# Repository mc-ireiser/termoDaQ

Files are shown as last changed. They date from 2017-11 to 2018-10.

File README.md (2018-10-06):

# termoDaQ

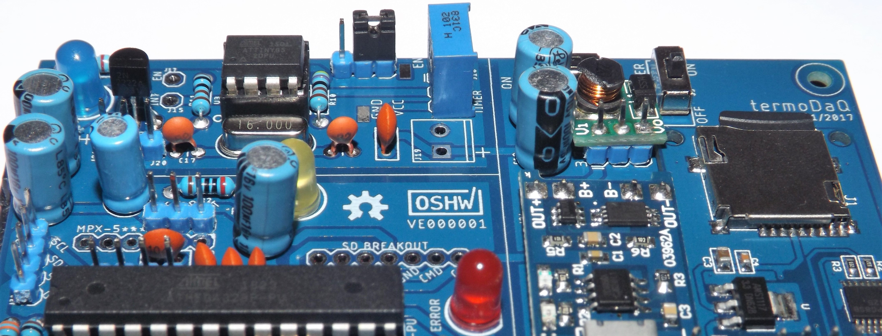
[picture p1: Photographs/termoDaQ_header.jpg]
Header


termoDaQ is a development board based on the [Arduino](https://www.arduino.cc/) architecture, uses an [ATmega328-P](http://ww1.microchip.com/downloads/en/DeviceDoc/Atmel-42735-8-bit-AVR-Microcontroller-ATmega328-328P_Summary.pdf) and an [ATtiny85](http://ww1.microchip.com/downloads/en/DeviceDoc/Atmel-2586-AVR-8-bit-Microcontroller-ATtiny25-ATtiny45-ATtiny85_Datasheet-Summary.pdf) for its operation.

This board was originally designed to help the work of oceanography students, serving as an instrument for the acquisition of physical variables (temperature, pressure) at surface level in bodies of fresh water, in order to detect changes that may affect the flora or fauna of ecosystems, automating the work of making measurements over time.

But it can serve many purposes since it has a connection for GPS receivers, pressure sensor, multiple temperature sensors (internal and external), two additional inputs for any analog sensor (such as rain, flow or UV) and SD card.

The function of the [ATtiny85](http://ww1.microchip.com/downloads/en/DeviceDoc/Atmel-2586-AVR-8-bit-Microcontroller-ATtiny25-ATtiny45-ATtiny85_Datasheet-Summary.pdf) is work as a timer to program the operation cycles of the equipment, reducing the energy consumption, which allows incrementing the operation time when the battery is used. To achieve this, activate and deactivate the sensors area.

The function of the [ATmega328-P](http://ww1.microchip.com/downloads/en/DeviceDoc/Atmel-42735-8-bit-AVR-Microcontroller-ATmega328-328P_Summary.pdf) is to control the sensors area, managing each of them to perform the measurement and data storage processes.

## Operation

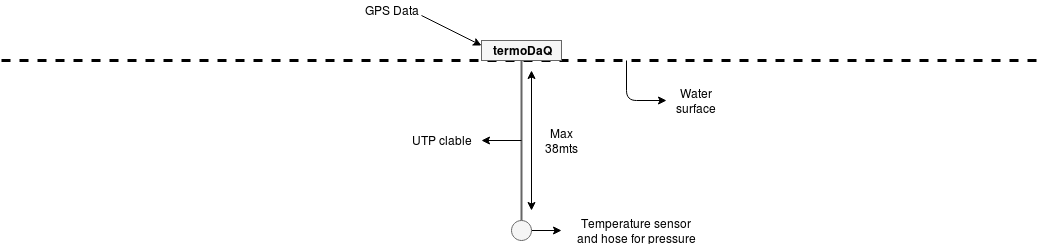
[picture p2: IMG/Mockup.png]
Operation


The board is divided into three parts

1) Power supply.
2) Energy management.
3) Sensors area.

In particular, I'm responsible for developing the energy management and the sensors area.

For the energy management, is used the [ATtiny85](http://ww1.microchip.com/downloads/en/DeviceDoc/Atmel-2586-AVR-8-bit-Microcontroller-ATtiny25-ATtiny45-ATtiny85_Datasheet-Summary.pdf) microcontroller to carry out cycles that enable or disable the sensors, cutting off the power in periods where no measurements are needed.

As for the sensors area, its function is to perform the measurements and store the data. Only one cycle at a time, at the end one signal is sent to the energy management area to cut the power.

## Pinout

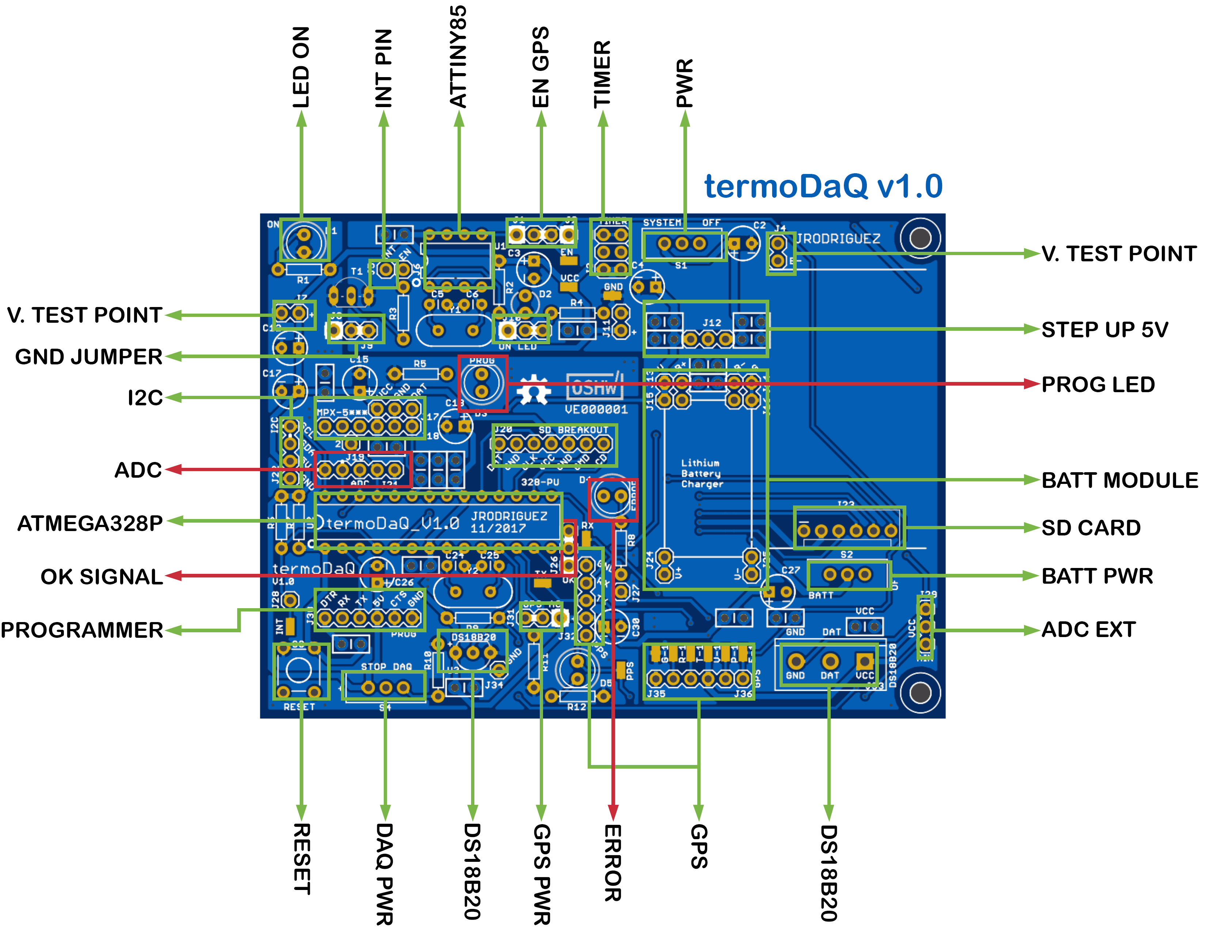
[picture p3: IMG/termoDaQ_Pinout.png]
Pinout


## Board specifications

All the source files are in this repository

- Board Size: 99.82 mm X 73.41 mm (X = 99.82, Y = 73.41)
- Number of layers: 2
- Number of drills: 311
- Number of vias: 47
- Number of signals: 146
- Minimum copper trace width: 0.41 mm
- Consumption: ~ 80mAh (currently under test)

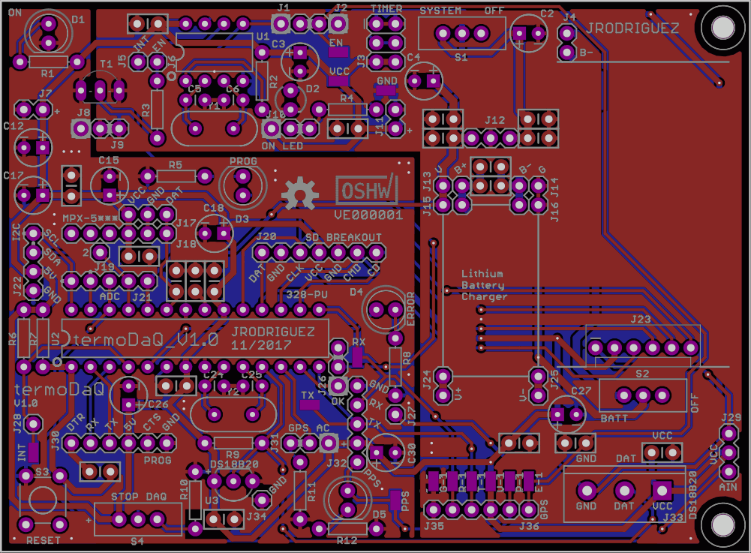
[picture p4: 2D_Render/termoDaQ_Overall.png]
Overall


### ATtiny85

|Name | Value |
| ---------- | ---------- |
|Operating Voltage Range (V) | 1.8 to 5.5 |
|Temperature Range (C) | -40 to 85 |
|CPU Speed (MIPS/DMIPS) | 20 |
|Pin Count | 8 |
|Program Memory Type | Flash |
|Program Memory Size (KB) | 8 |
|SRAM Bytes | 512 |
|Data EEPROM/HEF (bytes) | 512 |
|Digital Communication Peripherals | 1-SPI, 1-I2C |
|Capture/Compare/PWM Peripherals | 5PWM |
|Timers | 2 x 8-bit |
|Number of Comparators | 1 |

### ATmega328P

| Name | Value |
| ---------- | ---------- |
|Operating Supply Voltage | 1.8 V to 5.5 V |
|Temperature Range (C) | - 40 to 85 |
|Maximum Clock Frequency | 20 MHz |
|Pin count | 28 |
|Number of I/Os | 23 I/O |
|Program Memory Type | Flash |
|Program Memory Size | 32 kB |
|Data Bus Width | 8 bit |
|Data RAM Type | SRAM |
|Data RAM Size | 2 kB |
|Data ROM Type | EEPROM |
|Data ROM Size | 1 kB |
|Number of ADC Channels | 6 |
|ADC Resolution | 10 bit |
|Interface Type | I2C, SPI, USART |
|Number of Timers/Counters | 3 Timer |

## Translation

English translation using google translator.

If you wish, you can help me translate the readme file correctly.

## License

Creative Commons Attribution-ShareAlike 4.0 International Public License

Please go to the License section for more information. [Link](https://github.com/mc-ireiser/termoDaQ/tree/master/License)



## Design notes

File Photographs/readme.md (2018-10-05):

# Assembly and operation test

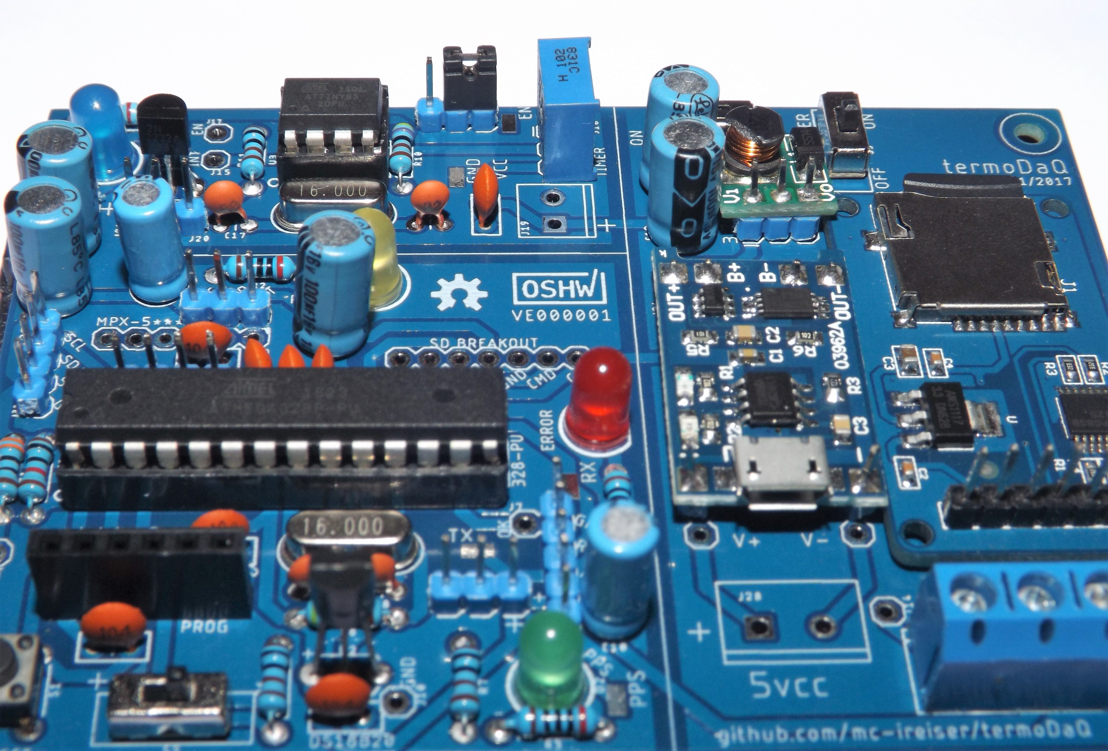
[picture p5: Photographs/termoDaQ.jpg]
Board Assembly


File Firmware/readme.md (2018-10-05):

# Attention

The firmware is under development.

All sensors were tested and work properly. [Picture](https://github.com/mc-ireiser/termoDaQ/blob/master/Photographs/termoDaQ.jpg).

Meanwhile you can perform tests or create your own code based on the [**arduino**](https://www.arduino.cc/reference/en/) architecture.

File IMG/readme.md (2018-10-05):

# Images

## Pinout

Pinout

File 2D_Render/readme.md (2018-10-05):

# 2D Render

2D rendering from source files.

## Top

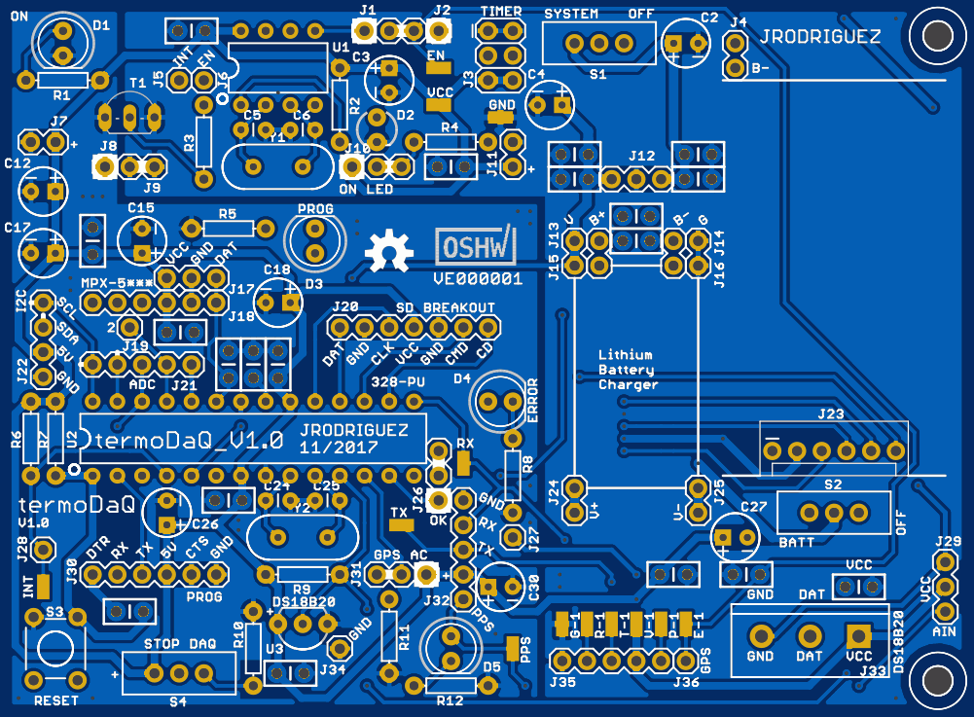
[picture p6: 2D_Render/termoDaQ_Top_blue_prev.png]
Top 2D Render


## Bottom

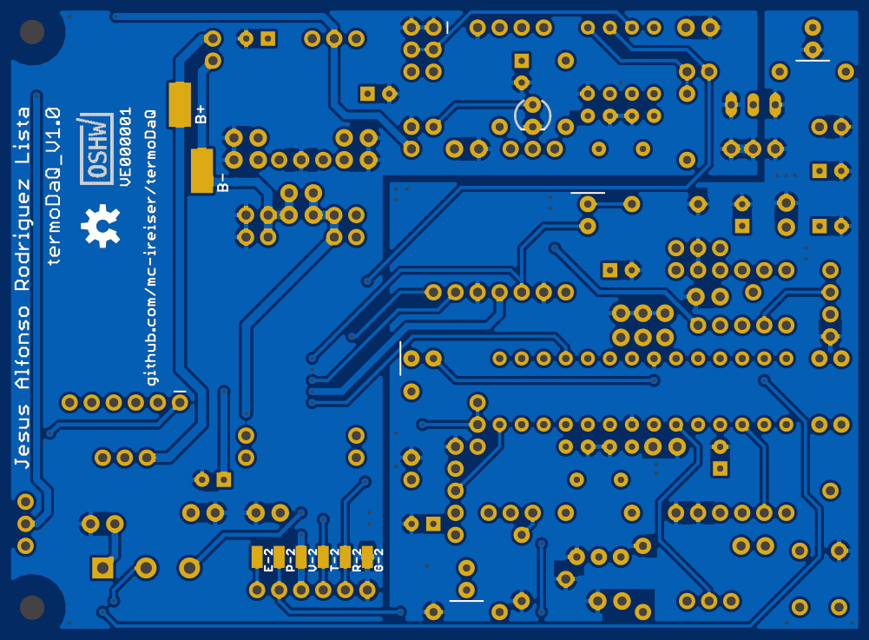
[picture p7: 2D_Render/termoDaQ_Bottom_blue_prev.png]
Bottom 2D Render


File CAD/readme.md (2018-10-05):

# Description of files

- .brd source file with the design of the PCB
- .sch source file with the schematics of the board

These files are licensed under: Creative Commons Attribution-ShareAlike 4.0 International Public License

## Schematics

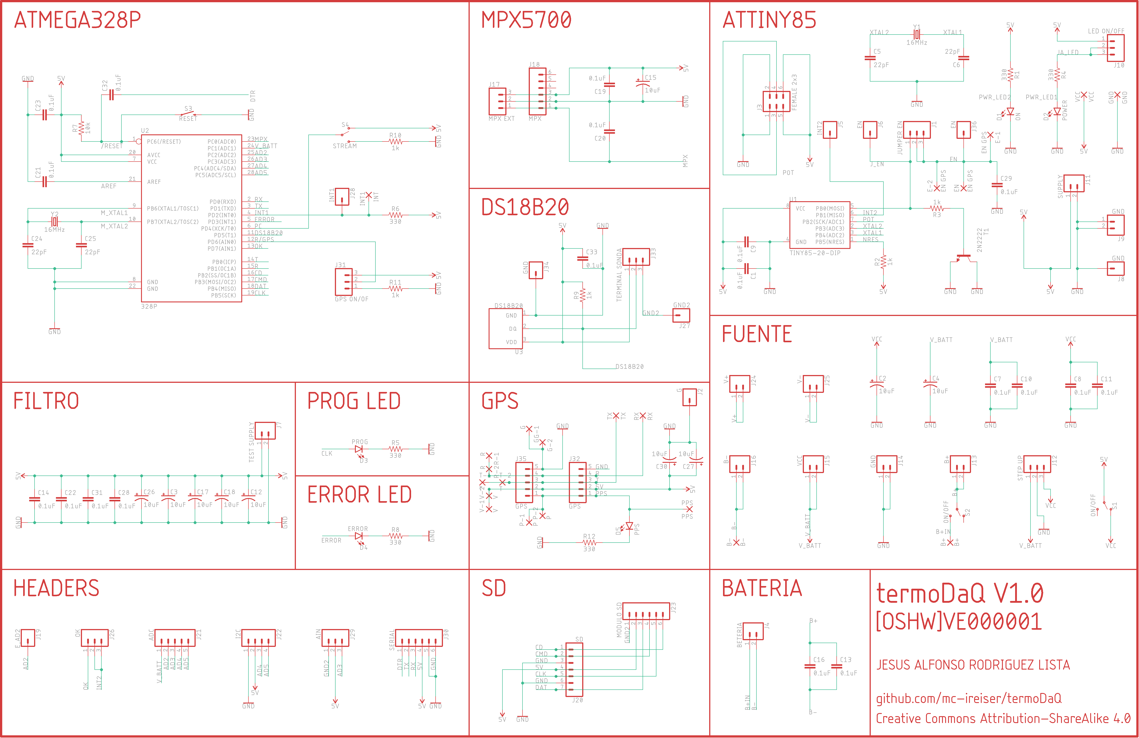
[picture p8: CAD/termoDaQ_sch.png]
Schematics


## Disclaimer

Last updated: October 05, 2018

(the "Service", files contained on this page)

Jesus Rodriguez assumes no responsibility for errors or omissions in the contents on the Service.

In no event shall Jesus Rodriguez be liable for any special, direct, indirect, consequential, or incidental damages or any damages whatsoever, whether in an action of contract, negligence or other tort, arising out of or in connection with the use of the Service or the contents of the Service. Jesus Rodriguez reserves the right to make additions, deletions, or modification to the contents on the Service at any time without prior notice.

This Disclaimer for Jesus Rodriguez is managed by TermsFeed Disclaimer Generator

Jesus Rodriguez does not warrant that the website is free of viruses or other harmful components.

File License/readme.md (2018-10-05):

# License

**termoDaQ** [OSHW] VE000001 by **Jesus Alfonso Rodriguez Lista**, is licensed under:

## Creative Commons Attribution-ShareAlike 4.0 International Public License

- File: `~/Licence/CC BY-SA 4.0.txt` - [read](https://github.com/mc-ireiser/termoDaQ/blob/master/License/CC%20BY-SA%204.0.txt)

- Source: https://creativecommons.org/licenses/by-sa/4.0



## Certified open source hardware

Link: https://certification.oshwa.org/ve000001.html

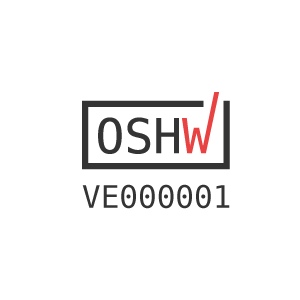
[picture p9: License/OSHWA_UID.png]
OSHWA UID VE000001


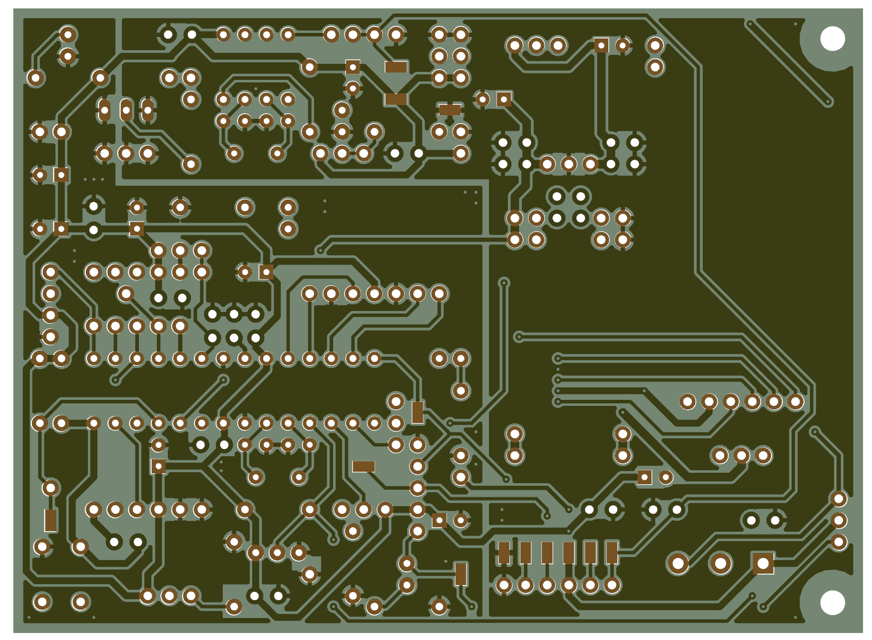
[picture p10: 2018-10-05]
2D_Render/termoDaQ_fr4_no-silk.png

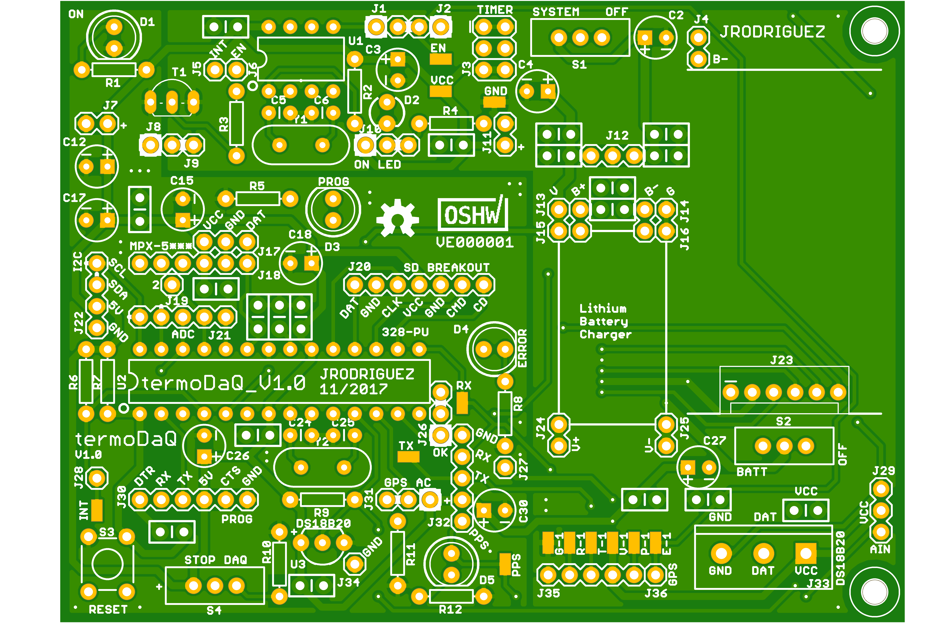
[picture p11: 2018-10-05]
2D_Render/termoDaQ_Top_green_prev.png

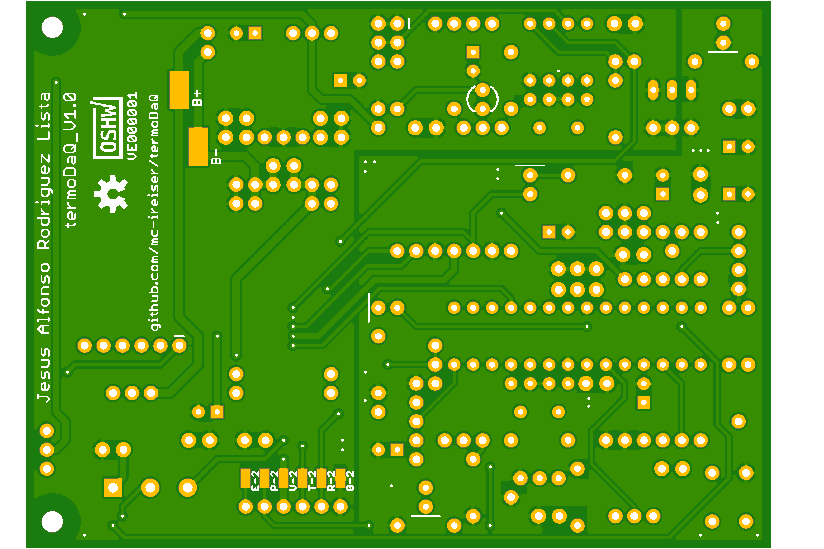
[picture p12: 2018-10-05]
2D_Render/termoDaQ_Bottom_green_prev.png

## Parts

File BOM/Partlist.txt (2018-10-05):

Partlist

Exported from termoDaQ.brd

EAGLE Version 9.1.3 Copyright (c) 1988-2018 Autodesk, Inc.

Assembly variant: 

Part     Value          Package                    Library                     Position (inch)       Orientation

C1       0.1uF          CAP-PTH-SMALL-KIT          SparkFun-Capacitors         (0.8 2.8)             R0
C2       10uF           CPOL-RADIAL-2.5MM-5MM      SparkFun-Capacitors         (2.8 2.75)            R180
C3       10uF           CPOL-RADIAL-2.5MM-5MM      SparkFun-Capacitors         (1.6 2.6)             R90
C4       10uF           CPOL-RADIAL-2.5MM-5MM      SparkFun-Capacitors         (2.25 2.5)            R0
C5       22pF           CAP-PTH-2.54               SparkFun-Capacitors         (1.05 2.4)            R0
C6       22pF           CAP-PTH-2.54               SparkFun-Capacitors         (1.25 2.4)            R0
C7       0.1uF          CAP-PTH-SMALL-KIT          SparkFun-Capacitors         (2.35 2.3)            R180
C8       0.1uF          CAP-PTH-SMALL-KIT          SparkFun-Capacitors         (2.85 2.3)            R0
C9       0.1uF          CAP-PTH-SMALL-KIT          SparkFun-Capacitors         (1.85 2.25)           R0
C10      0.1uF          CAP-PTH-SMALL-KIT          SparkFun-Capacitors         (2.35 2.2)            R180
C11      0.1uF          CAP-PTH-SMALL-KIT          SparkFun-Capacitors         (2.85 2.2)            R0
C12      10uF           CPOL-RADIAL-2.5MM-5MM      SparkFun-Capacitors         (0.2 2.15)            R0
C13      0.1uF          CAP-PTH-SMALL-KIT          SparkFun-Capacitors         (2.6 2.05)            R0
C14      0.1uF          CAP-PTH-SMALL-KIT          SparkFun-Capacitors         (0.4 1.95)            R90
C15      10uF           CPOL-RADIAL-2.5MM-5MM      SparkFun-Capacitors         (0.6 1.95)            R270
C16      0.1uF          CAP-PTH-SMALL-KIT          SparkFun-Capacitors         (2.6 1.95)            R0
C17      10uF           CPOL-RADIAL-2.5MM-5MM      SparkFun-Capacitors         (0.2 1.9)             R0
C18      10uF           CPOL-RADIAL-2.5MM-5MM      SparkFun-Capacitors         (1.15 1.7)            R0
C19      0.1uF          CAP-PTH-SMALL-KIT          SparkFun-Capacitors         (0.755 1.58)          R180
C20      0.1uF          CAP-PTH-SMALL-KIT          SparkFun-Capacitors         (0.95 1.45)           R90
C21      0.1uF          CAP-PTH-SMALL-KIT          SparkFun-Capacitors         (1.05 1.45)           R270
C22      0.1uF          CAP-PTH-SMALL-KIT          SparkFun-Capacitors         (1.15 1.45)           R90
C23      0.1uF          CAP-PTH-SMALL-KIT          SparkFun-Capacitors         (0.95 0.9)            R0
C24      22pF           CAP-PTH-2.54               SparkFun-Capacitors         (1.15 0.9)            R0
C25      22pF           CAP-PTH-2.54               SparkFun-Capacitors         (1.35 0.9)            R180
C26      10uF           CPOL-RADIAL-2.5MM-5MM      SparkFun-Capacitors         (0.7 0.85)            R270
C27      10uF           CPOL-RADIAL-2.5MM-5MM      SparkFun-Capacitors         (3 0.75)              R180
C28      0.1uF          CAP-PTH-SMALL-KIT          SparkFun-Capacitors         (2.75 0.6)            R0
C29      0.1uF          CAP-PTH-SMALL-KIT          SparkFun-Capacitors         (3.045 0.6)           R180
C30      10uF           CPOL-RADIAL-2.5MM-5MM      SparkFun-Capacitors         (2.05 0.55)           R180
C31      0.1uF          CAP-PTH-SMALL-KIT          SparkFun-Capacitors         (3.5 0.55)            R0
C32      0.1uF          CAP-PTH-SMALL-KIT          SparkFun-Capacitors         (0.55 0.45)           R180
C33      0.1uF          CAP-PTH-SMALL-KIT          SparkFun-Capacitors         (1.2 0.2)             R0
D1       ON             LED_5MM                    SparkFun-LED                (0.28 2.75)           R270
D2       POWER          LED_3MM                    SparkFun-LED                (1.55 2.4)            R270
D3       PROG           LED_5MM                    SparkFun-LED                (1.3 1.95)            R90
D4       ERROR          LED_5MM                    SparkFun-LED                (2.05 1.3)            R0
D5       PPS            LED_5MM                    SparkFun-LED                (1.85 0.3)            R270
J1       JUMPER EN      1X03                       SparkFun-Connectors         (1.5 2.8)             R0
J4       BETERIA        1X02                       SparkFun-Connectors         (3 2.75)              R270
J7       TEST SUPPLY    1X02                       SparkFun-Connectors         (0.25 2.35)           R180
J10      LED ON/OFF     1X03                       SparkFun-Connectors         (1.45 2.25)           R0
J11      SUPPLY         1X02                       SparkFun-Connectors         (2.1 2.25)            R90
J22      I2C            1X04                       SparkFun-Connectors         (0.2 1.4)             R90
J26      OK             1X03                       SparkFun-Connectors         (1.8 0.9)             R90
J30      SERIAL         1X06                       SparkFun-Connectors         (0.4 0.6)             R0
J31      GPS ON/OF      1X03                       SparkFun-Connectors         (1.55 0.6)            R0
J33      TERMINAL SONDA SCREWTERMINAL-5MM-3        SparkFun-Connectors         (3.5 0.35)            R180
R1       330            AXIAL-0.3                  SparkFun-Resistors          (0.28 2.6)            R180
R2       1k             AXIAL-0.3                  SparkFun-Resistors          (1.4 2.5)             R270
R3       1k             AXIAL-0.3                  SparkFun-Resistors          (0.85 2.35)           R90
R4       330            AXIAL-0.3                  SparkFun-Resistors          (1.85 2.35)           R0
R5       330            AXIAL-0.3                  SparkFun-Resistors          (0.95 2)              R180
R6       330            AXIAL-0.3                  SparkFun-Resistors          (0.15 1.15)           R90
R7       10k            AXIAL-0.3                  SparkFun-Resistors          (0.25 1.15)           R90
R8       330            AXIAL-0.3                  SparkFun-Resistors          (2.1 1)               R270
R9       1k             AXIAL-0.3                  SparkFun-Resistors          (1.25 0.6)            R180
R10      1k             AXIAL-0.3                  SparkFun-Resistors          (1.05 0.3)            R90
R11      1k             AXIAL-0.3                  SparkFun-Resistors          (1.6 0.35)            R270
R12      330            AXIAL-0.3                  SparkFun-Resistors          (1.85 0.15)           R180
S1       ON/OFF         SWITCH_SPDT_PTH_11.6X4.0MM SparkFun-Switches           (2.45 2.75)           R90
S2       ON/OFF         SWITCH_SPDT_PTH_11.6X4.0MM SparkFun-Switches           (3.4 0.85)            R270
S3       RESET          TACTILE_SWITCH_PTH_6.0MM   SparkFun-Switches           (0.25 0.3)            R270
S4       STREAM         SWITCH_SPDT_PTH_11.6X4.0MM SparkFun-Switches           (0.75 0.2)            R90
T1       2N2222         TO92-EBC-OVAL              adafruit                    (0.55 2.5)            R0
TX       TX             SMD1,27-2,54               wirepad                     (1.65 0.8)            R270
U1       TINY85-20-DIP  DIP08_MCU                  SparkFun-Retired            (1.15 2.65)           R0
U2       328P           DIP28                      SparkFun-IC-Microcontroller (1.05 1.15)           R0
U3       DS18B20        TO-92-AMMO                 SparkFun-Sensors            (1.25 0.4)            R180
Y1       16MHz          HC49US                     SparkFun-Clocks             (1.15 2.25)           R0
Y2       16MHz          HC49US                     SparkFun-Clocks             (1.25 0.75)           R0

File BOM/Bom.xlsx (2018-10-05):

ID | Name | Designator | Footprint | Quantity | Manufacturer Part | Manufacturer
11 | 328P | U2 | DIP28 | 1 | ATMEGA328P-PU | MICROCHIP
12 | 16MHz | Y2,Y1 | HC49US | 2 | E49A16E00000DE10C0 | HOSONIC
13 | 22pF | C24,C25,C5,C6 | CAP-PTH-2.54 | 4 | 22pf/50V 10% | ReliaPro
14 | 0.1uF | C21,C23,C32,C33,C19,C20,C9,C22,C1,C14,C31,C7,C28,C8,C11,C10,C29,C16,C13 | CAP-PTH-SMALL-KIT | 19 | CS1F5.6Y5V1A104Z | ReliaPro
15 | RESET | S3 | TACTILE_SWITCH_PTH_6.0MM | 1 | DTS-61K-V | DIP
16 | 10k | R7 | AXIAL-0.3 | 1 | MF1/2W-10KΩ±1% T52 | CCO
17 | PPS | D5 | LED_5MM | 1 | 5AW2UC | KENTO
18 | 330 | R12,R6,R8,R5,R1,R4 | AXIAL-0.3 | 6 | MF1/2W-330Ω±1% T52 | CCO
19 | DS18B20 | U3 | TO-92-AMMO | 1 | DS18B20+ | MAXIM
20 | 1k | R9,R11,R10,R3,R2 | AXIAL-0.3 | 5 | MF1/2W-1KΩ±1% T52 | CCO
21 | ERROR | D4 | LED_5MM | 1 | 5AW2UC | KENTO
22 | SERIAL | J30 | 1X06 | 1 | Female header 1*6p | BOOMELE
24 | STREAM | S4 | SWITCH_SPDT_PTH_11.6X4.0MM | 1
25 | INT1 | J28 | 1X01 | 1 | Header-Male-2.54_1x1 | ReliaPro
26 | MPX | J18 | 1X06 | 1 | MPX5700AP | NXP
27 | 10uF | C15,C12,C18,C17,C30,C2,C4,C3,C26,C27 | CPOL-RADIAL-2.5MM-5MM | 10 | 10uf/100V | ValuePro
28 | ADC | J21 | 1X05 | 1 | 210S-1*5P L=11.6MMGold-plated black | Ckmtw
29 | GPS ON/OF | J31 | 1X03 | 1 | Header2.54mm 1*3P | BOOMELE
30 | PROG | D3 | LED_5MM | 1 | 5AW2UC | KENTO
31 | TINY85-20-DIP | U1 | DIP08_MCU | 1 | ATTINY45-20PU | MICROCHIP
32 | 2N2222 | T1 | TO92-EBC-OVAL | 1 | 2N2222 | SEMTECH
33 | SUPPLY | J11 | 1X02 | 1 | 826629-2 | TE Connectivity
34 | FEMALE 2x3 | J3 | 2X3 | 1 | Precision potentiometer100Ω | ReliaPro
35 | INT2 | J5 | 1X01 | 1 | Header-Male-2.54_1x1 | ReliaPro
36 | ON | D1 | LED_5MM | 1 | 5AW2UC | KENTO
44 | ON/OFF | S1,S2 | SWITCH_SPDT_PTH_11.6X4.0MM | 2
45 | TEST SUPPLY | J7 | 1X02 | 1 | 826629-2 | TE Connectivity
46 | EN | J6,J36 | 1X01 | 2 | Header-Male-2.54_1x1 | ReliaPro
49 | MODULO SD | J23 | MOLEX-1X6 | 1 | Header-Male-2.54_1x6 | BOOMELE
50 | TERMINAL SONDA | J33 | SCREWTERMINAL-5MM-3 | 1
51 | GND2 | J27 | 1X01 | 1 | Header-Male-2.54_1x1 | ReliaPro
52 | GND | J34,J8 | 1X01 | 2 | Header-Male-2.54_1x1 | ReliaPro
53 | MPX EXT | J17 | 1X03 | 1 | Header2.54mm 1*3P | BOOMELE
54 | JUMPER EN | J1 | 1X03 | 1 | Header2.54mm 1*3P | BOOMELE
58 | I2C | J22 | 1X04 | 1 | 210S-1*4P L=11.6MMGold-plated black | Ckmtw
59 | AIN | J29 | 1X03 | 1 | Header2.54mm 1*3P | BOOMELE
60 | GPS | J32,J35 | 1X05 | 2 | 826629-2 | TE Connectivity
61 | POWER | D2 | LED_3MM | 1 | 3AG4HD01 | KENTO
62 | LED ON/OFF | J10 | 1X03 | 1 | Header2.54mm 1*3P | BOOMELE
63 | OK | J26 | 1X03 | 1 | Header2.54mm 1*3P | BOOMELE
65 | E_AD2 | J19 | 1X01 | 1 | Header-Male-2.54_1x1 | ReliaPro
67 | BETERIA | J4 | 1X02 | 1 | 826629-2 | TE Connectivity
69 | G | J2 | 1X01 | 1 | Header-Male-2.54_1x1 | ReliaPro

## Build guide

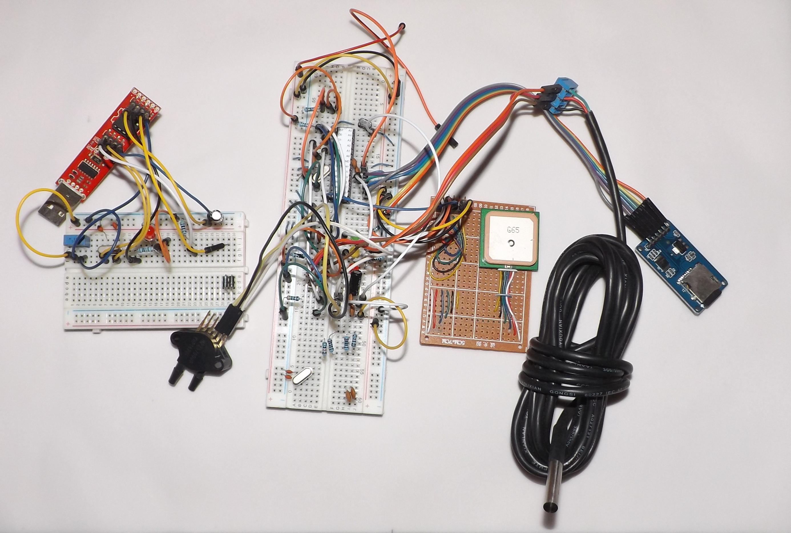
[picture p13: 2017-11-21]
Photographs/Protoboard Assembly.jpg

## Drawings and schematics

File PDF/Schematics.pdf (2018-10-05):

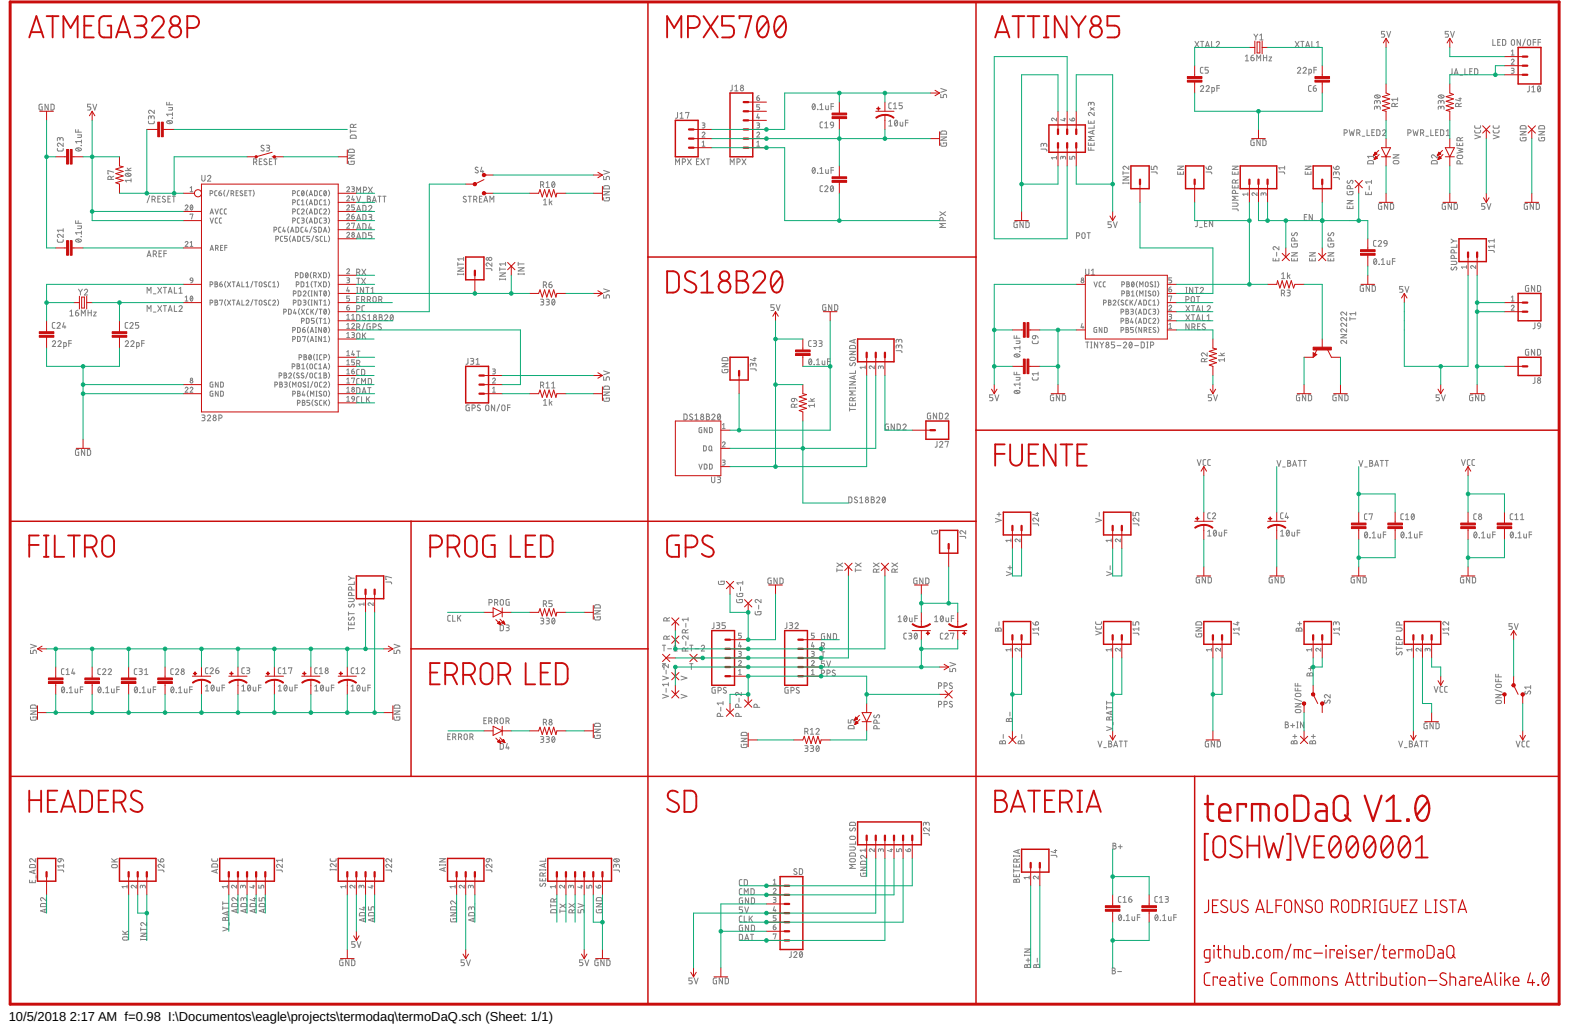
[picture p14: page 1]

10/5/2018 2:17 AM f=0.98 I:\Documentos\eagle\projects\termodaq\termoDaQ.sch (Sheet: 1/1)

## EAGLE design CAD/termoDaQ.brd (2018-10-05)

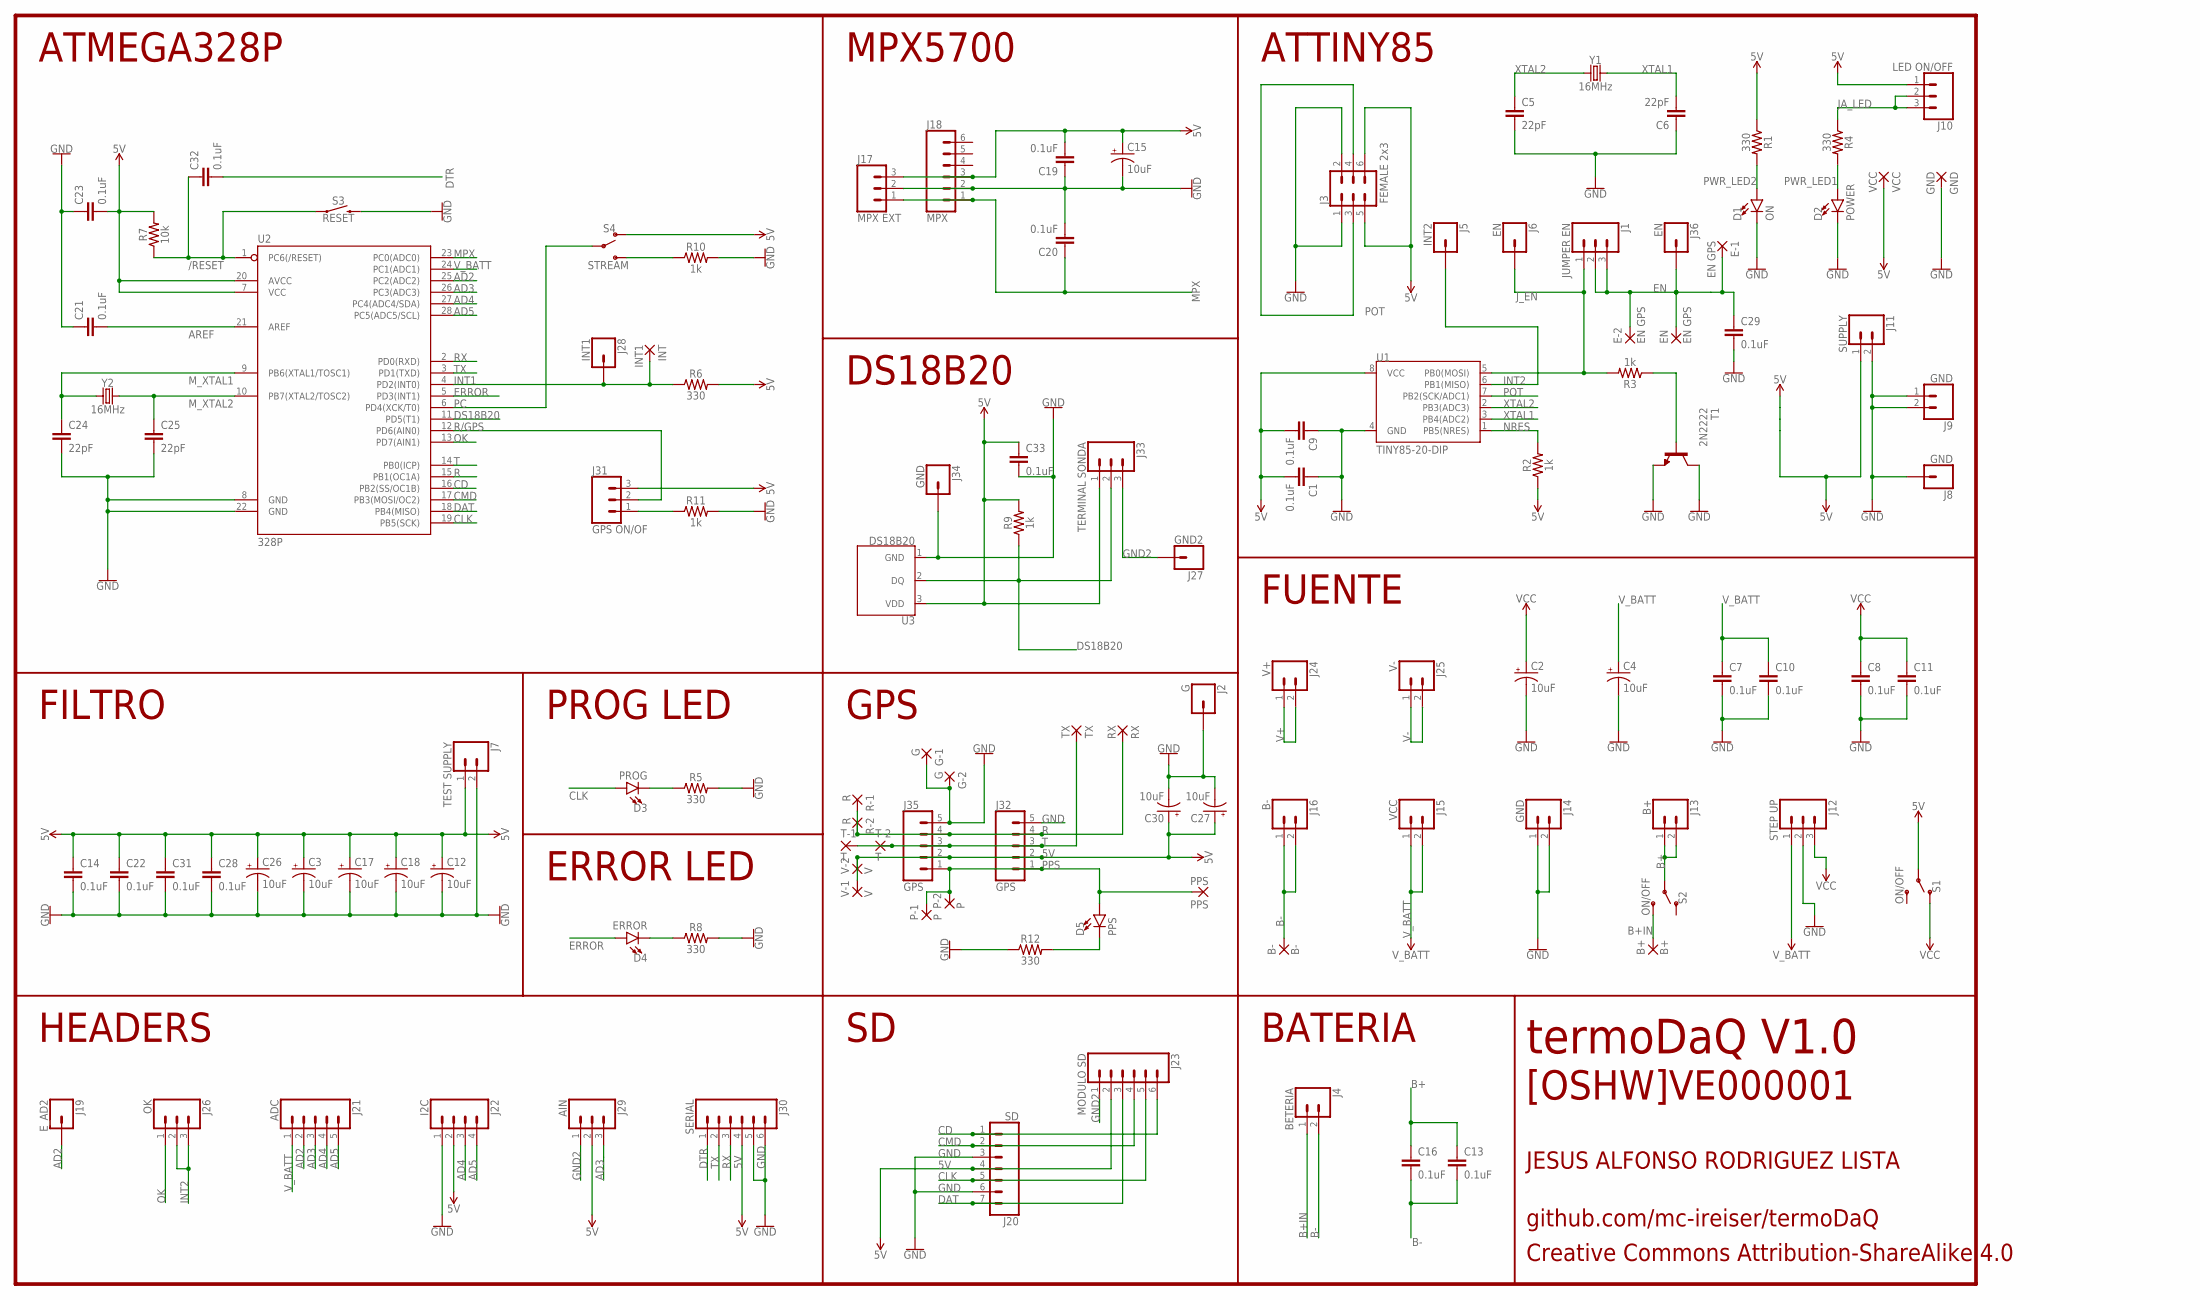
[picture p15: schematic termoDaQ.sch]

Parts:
B+: B+; SMD2,54-5,08
B-: B-; SMD2,54-5,08
C1, C7, C8, C9, C10, C11, C13, C14, C16, C19, C20, C21, C22, C23, C28, C29, C31, C32, C33: 0.1uF; CAP-PTH-SMALL-KIT
C2, C3, C4, C12, C15, C17, C18, C26, C27, C30: 10uF; CPOL-RADIAL-2.5MM-5MM
C5, C6, C24, C25: 22pF; CAP-PTH-2.54
D1: ON; LED_5MM
D2: POWER; LED_3MM
D3: PROG; LED_5MM
D4: ERROR; LED_5MM
D5: PPS; LED_5MM
E-1, E-2: EN GPS; SMD1,27-2,54
EN: EN GPS; SMD1,27-2,54
G-1, G-2: G; SMD1,27-2,54
GND: GND; SMD1,27-2,54
INT: INT1; SMD1,27-2,54
J1: JUMPER EN; 1X03
J2: G; 1X01
J3: FEMALE 2x3; 2X3
J4: BETERIA; 1X02
J5: INT2; 1X01
J6, J36: EN; 1X01
J7: TEST SUPPLY; 1X02
J8, J34: GND; 1X01
J9, J14: GND; 1X02
J10: LED ON/OFF; 1X03
J11: SUPPLY; 1X02
J12: STEP UP; 1X03
J13: B+; 1X02
J15: VCC; 1X02
J16: B-; 1X02
J17: MPX EXT; 1X03
J18: MPX; 1X06
J19: E_AD2; 1X01
J20: SD; 1X07
J21: ADC; 1X05
J22: I2C; 1X04
J23: MODULO SD; MOLEX-1X6
J24: V+; 1X02
J25: V-; 1X02
J26: OK; 1X03
J27: GND2; 1X01
J28: INT1; 1X01
J29: AIN; 1X03
J30: SERIAL; 1X06
J31: GPS ON/OF; 1X03
J32, J35: GPS; 1X05
J33: TERMINAL SONDA; SCREWTERMINAL-5MM-3
P-1, P-2: P; SMD1,27-2,54
PPS: PPS; SMD1,27-2,54
R1, R4, R5, R6, R8, R12: 330; AXIAL-0.3
R2, R3, R9, R10, R11: 1k; AXIAL-0.3
R7: 10k; AXIAL-0.3
R-1, R-2: R; SMD1,27-2,54
RX: RX; SMD1,27-2,54
S1, S2: ON/OFF; SWITCH_SPDT_PTH_11.6X4.0MM
S3: RESET; TACTILE_SWITCH_PTH_6.0MM
S4: STREAM; SWITCH_SPDT_PTH_11.6X4.0MM
T1: 2N2222; TO92-EBC-OVAL
T-1, T-2: T; SMD1,27-2,54
TX: TX; SMD1,27-2,54
U1: TINY85-20-DIP; DIP08_MCU
U2: 328P; DIP28
U3: DS18B20; TO-92-AMMO
V-1, V-2: V; SMD1,27-2,54
VCC: VCC; SMD1,27-2,54
Y1, Y2: 16MHz; HC49US

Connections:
5V: C1.2, C3.1 (+), C9.2, C12.1 (+), C14.1, C15.1 (+), C17.1 (+), C18.1 (+), C19.2, C22.1, C23.2, C26.1 (+), C27.1 (+), C28.1, C30.1 (+), C31.1, C33.1, J3.5, J3.6, J7.1, J10.1, J11.1, J17.3, J18.3, J20.4, J22.2, J23.2, J29.2, J30.4, J31.3, J32.2, J33.1, J35.2, R1.P$1 (1), R2.P$1 (1), R6.P$2 (2), R7.P$2 (2), R9.P$2 (2), S1.2, S4.1 (O), U1.8 (VCC), U2.7 (VCC), U2.20 (AVCC), U3.3 (VDD), V-1.1, V-2.1, VCC.1
/RESET: C32.1, R7.P$1 (1), S3.1, U2.1 (PC6(/RESET))
AD2: J19.1, J21.2, U2.25 (PC2(ADC2))
AD3: J21.3, J29.3, U2.26 (PC3(ADC3))
AD4: J21.4, J22.3, U2.27 (PC4(ADC4/SDA))
AD5: J21.5, J22.4, U2.28 (PC5(ADC5/SCL))
AREF: C21.2, U2.21 (AREF)
B+: C13.1, C16.1, J13.1, J13.2, S2.2
B+IN: B+.1, J4.1, S2.3 (S)
B-: B-.1, C13.2, C16.2, J4.2, J16.1, J16.2
CD: J20.1, J23.6, U2.16 (PB2(SS/OC1B))
CLK: D3.A, J20.5, J23.5, U2.19 (PB5(SCK))
CMD: J20.2, J23.4, U2.17 (PB3(MOSI/OC2))
DAT: J20.7, J23.3, U2.18 (PB4(MISO))
DS18B20: J33.2, R9.P$1 (1), U2.11 (PD5(T1)), U3.2 (DQ)
DTR: C32.2, J30.1
EN: C29.1, E-1.1, E-2.1, EN.1, J1.2, J1.3, J36.1
ERROR: D4.A, U2.5 (PD3(INT1))
GND: C1.1, C2.2 (-), C3.2 (-), C4.2 (-), C5.2, C6.1, C7.2, C8.2, C9.1, C10.2, C11.2, C12.2 (-), C14.2, C15.2 (-), C17.2 (-), C18.2 (-), C19.1, C20.2, C21.1, C22.2, C23.1, C24.2, C25.2, C26.2 (-), C27.2 (-), C28.2, C29.2, C30.2 (-), C31.2, C33.2, D1.K (C), D2.K (C), G-1.1, G-2.1, GND.1, J2.1, J3.1, J3.2, J7.2, J8.1, J9.1, J9.2, J11.2, J12.2, J14.1, J14.2, J17.2, J18.2, J20.3, J20.6, J22.1, J30.5, J30.6, J32.5, J34.1, J35.5, R5.P$2 (2), R8.P$2 (2), R10.P$2 (2), R11.P$2 (2), R12.P$1 (1), S3.3 (2), T1.C, T1.E, U1.4 (GND), U2.8 (GND), U2.22 (GND), U3.1 (GND)
GND2: J23.1, J27.1, J29.1, J33.3
INT1: INT.1, J28.1, R6.P$1 (1), U2.4 (PD2(INT0))
INT2: J5.1, J26.2, J26.3, U1.6 (PB1(MISO))
JA_LED: J10.2, J10.3, R4.P$1 (1)
J_EN: J1.1, J6.1, R3.P$2 (2), U1.5 (PB0(MOSI))
MPX: C20.1, J17.1, J18.1, U2.23 (PC0(ADC0))
M_XTAL1: C24.1, U2.9 (PB6(XTAL1/TOSC1)), Y2.1
M_XTAL2: C25.1, U2.10 (PB7(XTAL2/TOSC2)), Y2.2
unnamed: D3.K (C), R5.P$1 (1)
unnamed: D5.K (C), R12.P$2 (2)
unnamed: D4.K (C), R8.P$1 (1)
unnamed: J31.1, R11.P$1 (1)
unnamed: R10.P$1 (1), S4.3 (S)
unnamed: R3.P$1 (1), T1.B
NRES: R2.P$2 (2), U1.1 (PB5(NRES))
OK: J26.1, U2.13 (PD7(AIN1))
PC: S4.2, U2.6 (PD4(XCK/T0))
POT: J3.3, J3.4, U1.7 (PB2(SCK/ADC1))
PPS: D5.A, J32.1, J35.1, P-1.1, P-2.1, PPS.1
PWR_LED1: D2.A, R4.P$2 (2)
PWR_LED2: D1.A, R1.P$2 (2)
R: J32.4, J35.4, R-1.1, R-2.1, RX.1, U2.15 (PB1(OC1A))
R/GPS: J31.2, U2.12 (PD6(AIN0))
RX: J30.3, U2.2 (PD0(RXD))
T: J32.3, J35.3, T-1.1, T-2.1, TX.1, U2.14 (PB0(ICP))
TX: J30.2, U2.3 (PD1(TXD))
V+: J24.1, J24.2
V-: J25.1, J25.2
VCC: C2.1 (+), C8.1, C11.1, J12.3, S1.1 (O)
V_BATT: C4.1 (+), C7.1, C10.1, J12.1, J15.1, J15.2, J21.1, U2.24 (PC1(ADC1))
XTAL1: C6.2, U1.3 (PB4(ADC2)), Y1.2
XTAL2: C5.1, U1.2 (PB3(ADC3)), Y1.1

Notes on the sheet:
FUENTE
ATTINY85
ATMEGA328P
HEADERS
JESUS ALFONSO RODRIGUEZ LISTA
GPS
DS18B20
MPX5700
PROG LED
FILTRO
ERROR LED
BATERIA
[OSHW]VE000001
github.com/mc-ireiser/termoDaQ
Creative Commons Attribution-ShareAlike 4.0
termoDaQ V1.0

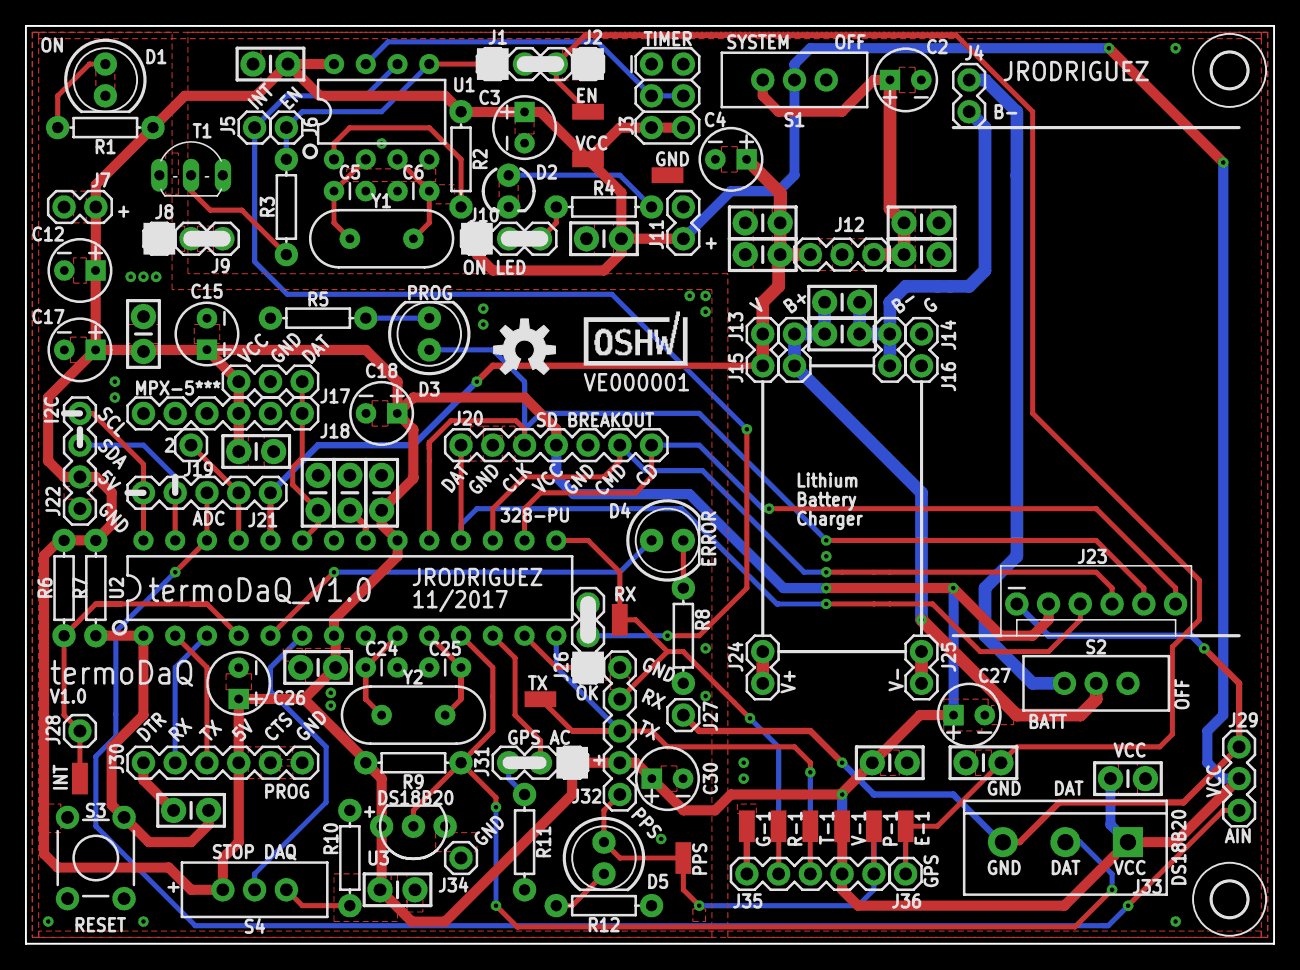
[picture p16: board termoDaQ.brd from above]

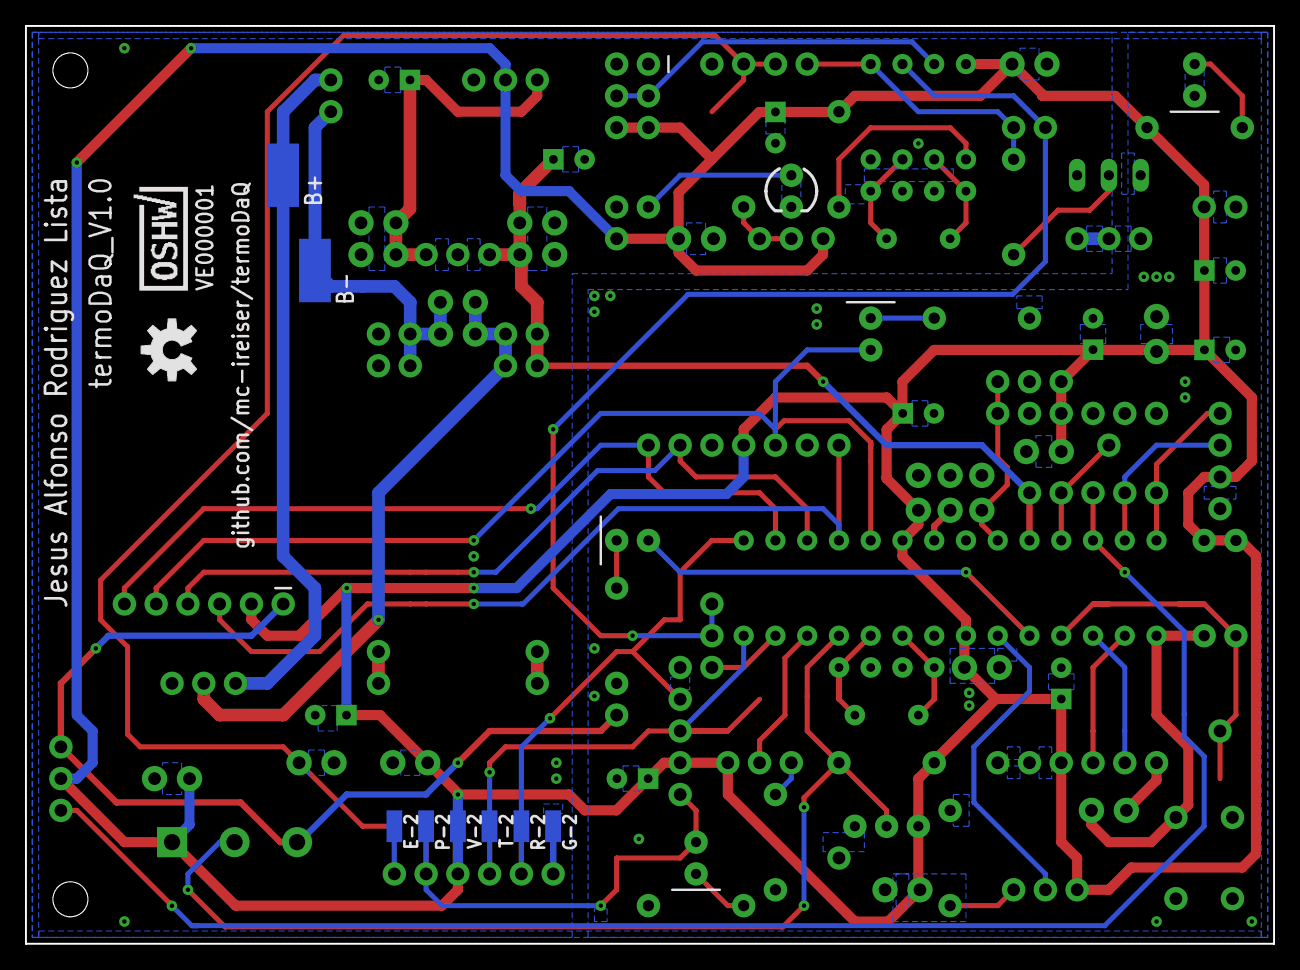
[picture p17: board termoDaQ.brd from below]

Board: 2 copper layers, 99.8 x 73.4 mm, 123 parts (10 on the bottom side), 51 nets.

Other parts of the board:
U$1, U$100: OSHW-LOGO-M
U$2, U$101: CERT-SMALL-SILK
U$3, U$4: 2,8

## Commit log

2017-11-21 Source files .brd and .sch from Eagle 8.4
    [termoDaQ.brd, termoDaQ.sch]
2017-11-21 PDF files of board and Schematics
2017-11-21 Proroboard Assembly full test
2017-11-21 Link to test assembly img
2017-11-25 Source files update
    [termoDaQ.brd, termoDaQ.sch]
2017-11-25 BOM on ods format
    [Bom.ods]
2017-11-26 Important update, start the manufacturing process in PCB
2018-01-19 Photographs of the assembled board
2018-01-19 PCB assembled
2018-10-05 Source files, Update
    [termoDaQ.brd, termoDaQ.sch]
2018-10-05 Update, Board specifications

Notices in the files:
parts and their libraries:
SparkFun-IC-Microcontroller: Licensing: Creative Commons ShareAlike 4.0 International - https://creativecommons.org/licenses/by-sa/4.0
